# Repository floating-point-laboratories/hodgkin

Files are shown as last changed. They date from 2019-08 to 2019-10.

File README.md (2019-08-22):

# Project Hodgkin
Project Hodgkin is an open-source (semi) Arduino Nano compatible microcontroller development board that is developed to IEC 60601 standards for 2xMOPP (methods of patient protection) isolation. It is intended for educational settings to enable students and enthusiasts to safely interface with biopotential amplifier circuits.

**Will this device be IEC 60601 certified / FDA cleared / etc.?**
*Due to the nature of this device's application, which is to enable students to interface with biomedical electronics which they have designed and built themselves, it is not practical to pursue any form of formal medical device certification. This device's performance will depend entirely on the quality of the circuits that it is attached to; it therefore cannot and should not be used as a substitute for any medical device for diagnostic or therapeutic purposes. The intention of this project is to provide a safe interface between these experimental circuits and a computer via USB interface so that users are not exposed to dangerous voltages or currents in the case of PC power supply failure or mains power surge.*

**What do you mean "semi" Arduino Nano compatible?**
*This device is planned to share a pinout, footprint, and firmware with the Arduino Nano V3.0 (based on the ATmega328p microcontroller). However, some changes will be necessary to ensure safe operation of the device while maintaining low cost. These include the inability to draw microcontroller power from the on-board USB port, and incompatibility with shields / expansion boards which are connected to mains power.*

**Why use an optical link? Why not use a wireless connection like BLE?**
*This is something that was certainly considered, but was ultimately abandoned in favor of a direct optical serial link for three primary reasons:*

*1. Cost. The goal for this project is to meet the necessary safety requirements without dramatically adding to the cost of an Arduino Nano. Obviously some added costs are unavoidable, but a full RF solution was deemed an uneccessary cost.*

*2. Stability. Since this project is intended as a direct Aduino Nano substitute for use by students, it was important to us that it behave as similarly to a stock Arduino as possible. This means plug-and-play direct USB-to-serial simplicity whenever possible.*

*3. Security. Athough this device is not intended for use as a medical device, it is built with similar design philosophies in mind. In general, wireless solutions are typically not implemented in medical devices unless there is a compelling reason to do so to avoid potential data leaks / HIPAA violations.*

**When can I purchase this device?**
*This device is planned for inclusion in the electronics kit given to all students enrolled in SBEE 2020. Standalone sale of the device will certainly be considered if there is a demand for it. In the meantime, you are welcome to build one yourself using the files available in this repository.*

## About The Shoulders of Giants
In 1676, Isaac Newton, one of the most influential mathematicians and scientists of all time, famously wrote:

> "If I have seen further, it is by standing on the shoulders of giants."

The Shoulders of Giants, Inc. (TSoG) is a nonprofit (501(c)(3)) organization founded in 2013 on a vision that world-class science education should be available to all students of all ages. Since 2015, The Shoulders of Giants has offered an immersive, ongoing mentorship program for dedicated students who would like the opportunity to study more closely under the guidance of Dr. Steven J. Foland. This program is designed to provide middle and high school students with a broad foundation of knowledge and skills across science and engineering disciplines, experience working and communicating in a professional environment, and helps them develop the study habits necessary to achieve success at the university level and beyond.

In 2019, this world-class program became available to students everywhere with the launch of TSoG.tv. This online platform, created in collaboration between The Shoulders of Giants, Inc. and its sister-company Floating Point Laboratories, LLC, provides at-home exercises, live-streaming, and project support to students anywhere in the world.

## About #SBEE2020
Since 2015, The Shoulders of Giants has offered its flagship summer program, the Summer Biomedical Engineering Experience (SBEE) to high school students interested in exploring careers in biomedical engineering and related medical sciences. The original contents of the program were 60 hours of rigorous curriculum covering biomedical electronics, mechanical CAD and 3D printing, and microcontroller programming. Through this program, nearly 400 students have designed and built their own electromyograph (EMG) controlled prosthetic hands. 

In spring 2019, TSoG co-founder and Floating Point Laboratories managing director Dr. Steven J. Foland [announced an initiative](https://www.youtube.com/watch?v=rmPsDaRs3cc) to develop the SBEE curriculum into a TSoG.tv experience for students around the world in summer 2020. This has become known as the #SBEE2020 initiative. Dr. Foland hosted a successful 24-hour livestream fundraiser on June 29-30th 2019, teaching a prototype SBEE 2020 curriculum in one marathon session which can be viewed [here](https://www.tsogiants.org/2019/07/02/24-hour-challenge-physiological-signals-and-biomedical-electronics/). 

As of August 2019, development for SBEE 2020 is currently underway. In order to best serve the community, several new devices need to be developed to provide safe, affordable access to the technologies necessary for students to explore and interface with human biosignals. Among these are: Project Hodgkin, an inexpensive Arduino compatible microcontroller development board built to follow IEC 60601 safety standards; and Project Huxley, a USB oscilloscope developed with biomedical applications and safety standards in mind.

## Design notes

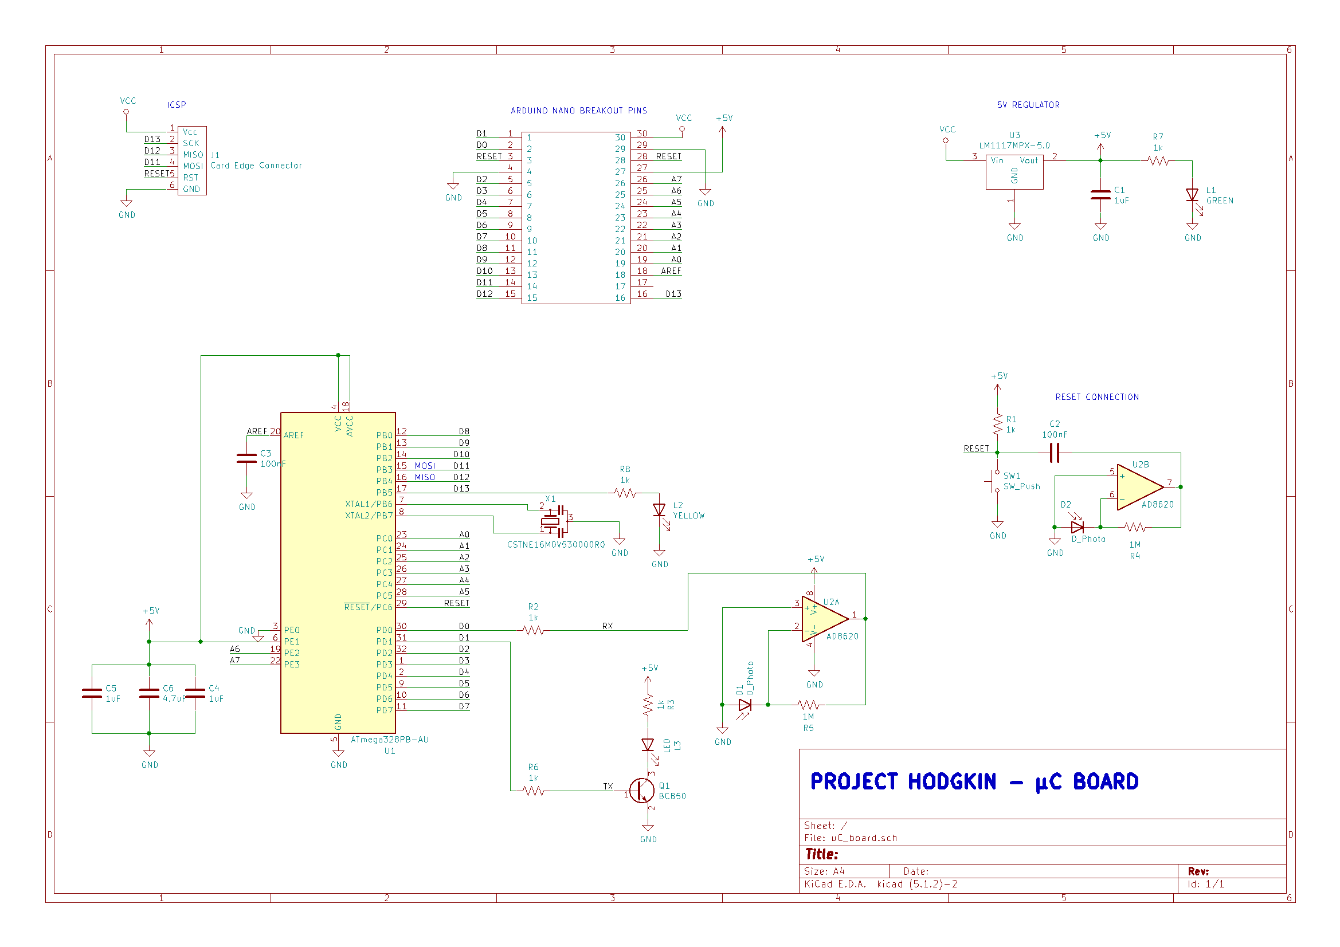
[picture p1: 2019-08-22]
_Media/uC_Board_Schematic.png

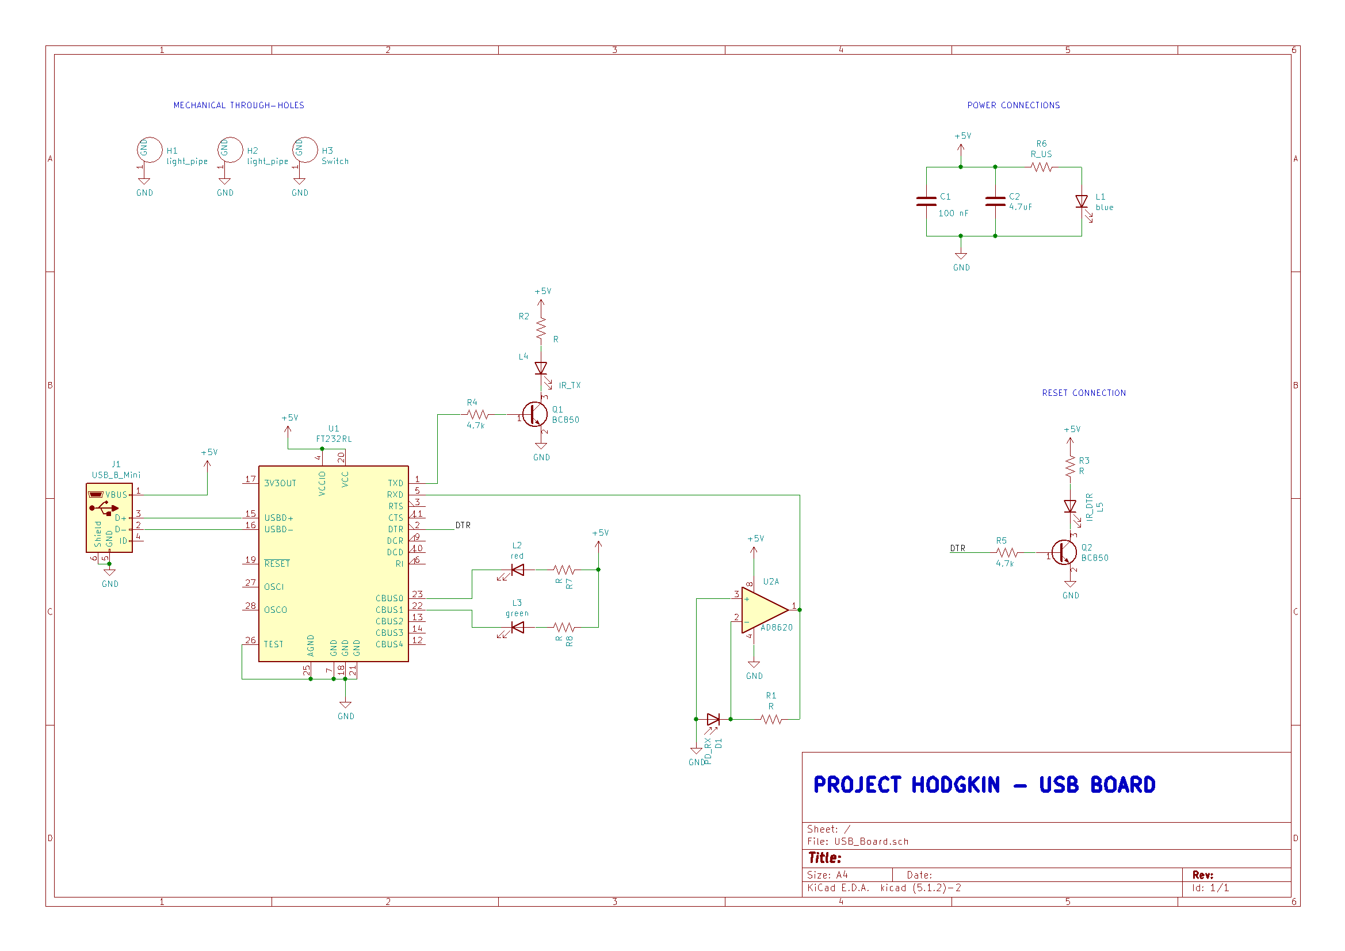
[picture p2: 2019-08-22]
_Media/USB_Board_Schematic.png

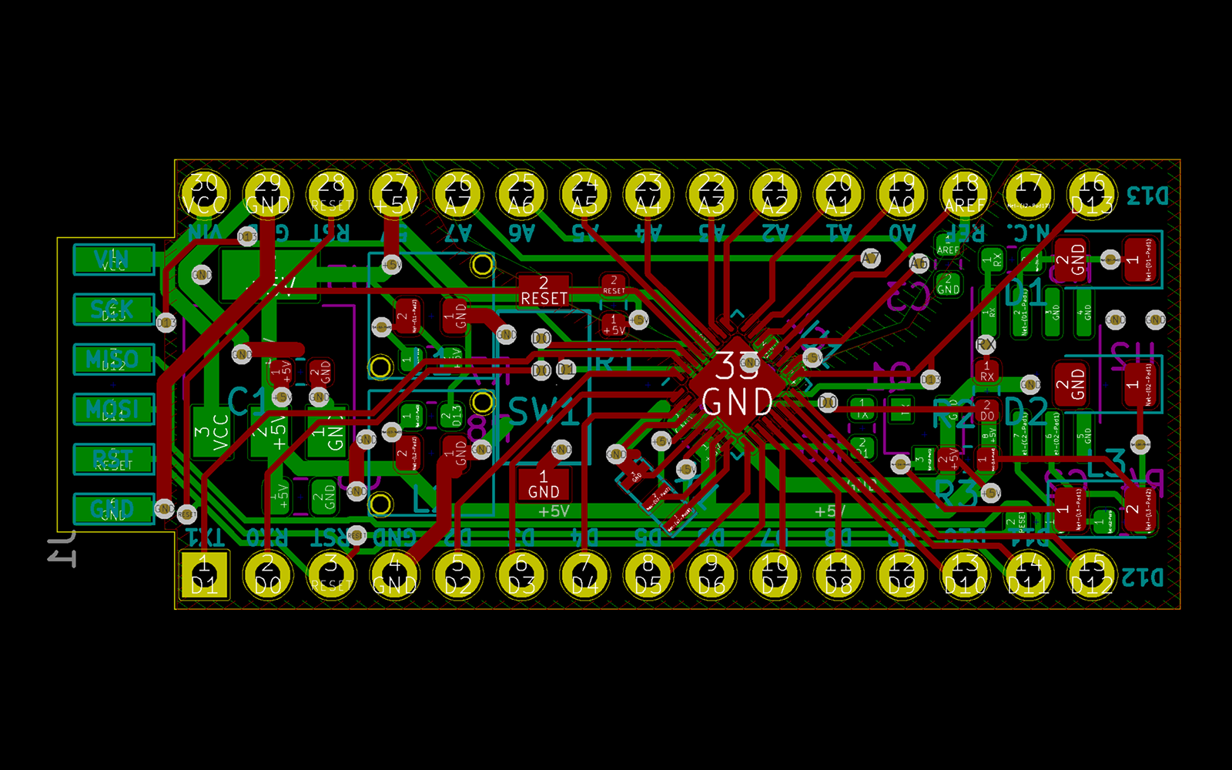
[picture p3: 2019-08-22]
_Media/uC_Board_Layout.png

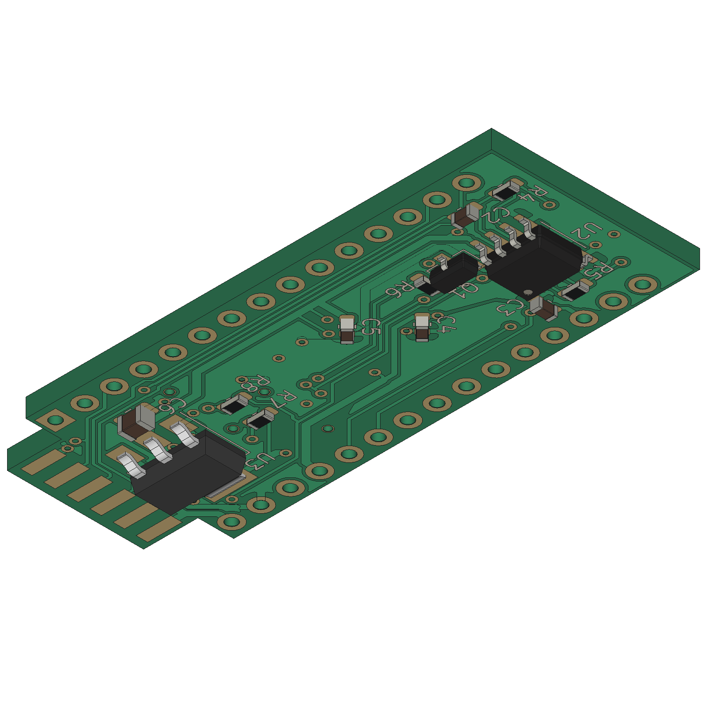
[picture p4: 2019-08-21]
_Media/uC_Board_bottom.png

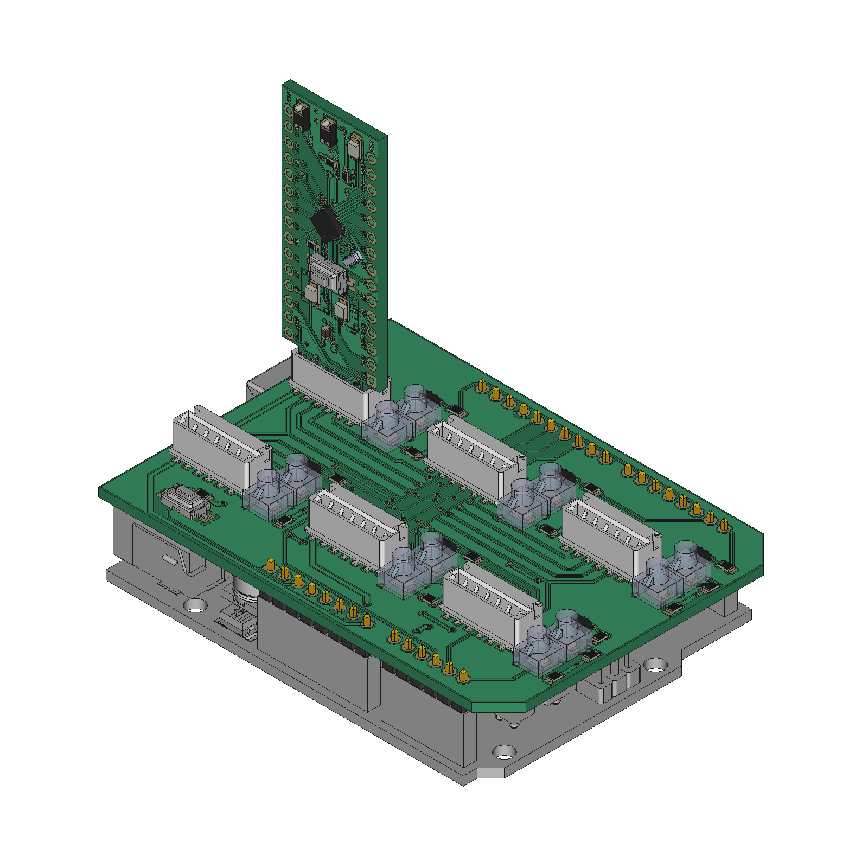
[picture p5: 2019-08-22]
_Media/ICSP_Board_withuC.png

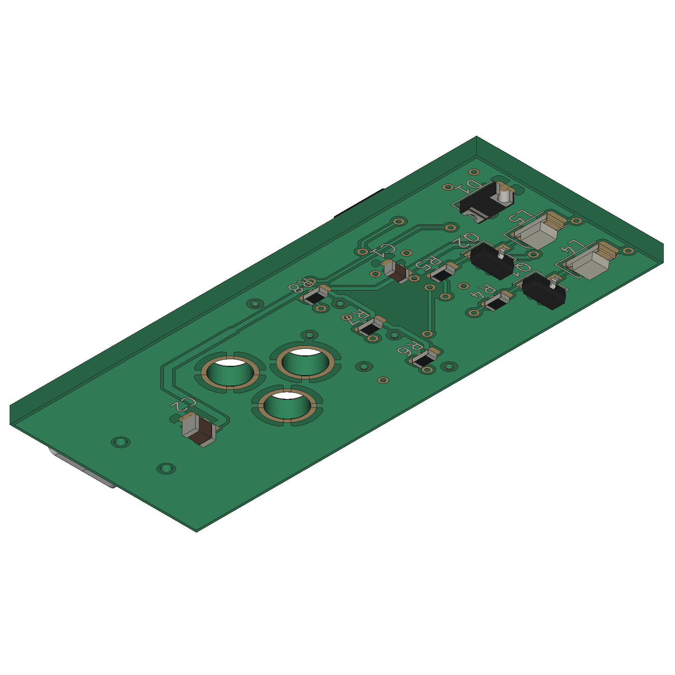
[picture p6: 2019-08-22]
_Media/USB_Board_Bottom.png

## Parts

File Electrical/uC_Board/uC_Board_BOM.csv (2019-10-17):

Description | Manufacturer | Man. Part # | Distributor | Dist. Part # | Link | Unit Price (@ 1) | Unit Price (@ 1000) | Quantity | Cost (@ 1) | Cost (@ 1000)
ATMEGA328 uC | Micochip Technology / Atmel | ATMEGA328PB-AU | Mouser | 556-ATMEGA328PB-AU | https://www.mouser.com/ProductDetail/Microchip-Technology-Atmel/ATMEGA328PB-AU?qs=jy4bLUHv09hbFONgGrqPbw%3D%3D | $1.38 | $1.150 | 1 | $1.38 | $1.150
Precision Transimpedance Amp | Texas Instruments | OPA2381AIDGKR | Mouser | 595-OPA2381AIDGKR | https://www.mouser.com/ProductDetail/Texas-Instruments/OPA2381AIDGKR | $2.68 | $1.410 | 1 | $2.68 | $1.410
IR Photodiode | Wurth Elektronik | 1541201EEA400 | Mouser | 710-1541201EEA400 | https://www.mouser.com/ProductDetail/Wurth-Elektronik/1541201EEA400 | $0.54 | $0.330 | 2 | $1.08 | $0.660
IR LED | Stanley Electric | TAN1105W-TR | Mouser | 327-TAN1105WTR | https://www.mouser.com/ProductDetail/Stanley-Electric/TAN1105W-TR | $0.37 | $0.123 | 1 | $0.37 | $0.123
NPN BJT | ON Semiconductor | BC850CLT1G | Mouser | 863-BC850CLT1G | https://www.mouser.com/ProductDetail/ON-Semiconductor/BC850CLT1G | $0.10 | $0.020 | 1 | $0.10 | $0.020
3.3V LDO Regulator | Texas Instruments | LM1117MPX-5.0/NOPB | Mouser | 926-LM1117MPX5.0NOPB | https://www.mouser.com/ProductDetail/Texas-Instruments/LM1117MPX-50-NOPB?qs=X1J7HmVL2ZE1O12Qsl7F9g%3D%3D | $1.10 | $0.501 | 1 | $1.10 | $0.501
16MHz oscillator | Murata Electronics | CSTNE16M0V530000R0 | Mouser | 81-CSTNE16M0V530000R | https://www.mouser.com/ProductDetail/Murata-Electronics/CSTNE16M0V530000R0 | $0.51 | $0.269 | 1 | $0.51 | $0.269
pushbutton switch | C&K | PTS636 SK25 SMTR LFS | Mouser | 611-PTS636SK25SMTRLF | https://www.mouser.com/ProductDetail/CK/PTS636-SK25-SMTR-LFS | $0.13 | $0.076 | 1 | $0.13 | $0.076
light pipe | Bivar | VLP-650-F | Digi-Key | 492-2287-ND | https://www.digikey.com/product-detail/en/bivar-inc/VLP-650-F/492-2287-ND/4500883 | $0.53 | $0.170 | 2 | $1.06 | $0.340
1uF capacitor 0603 |  |  |  |  |  |  |  | 3
4.7uF capacitor 0805 |  |  |  |  |  |  |  | 1
100nF capacitor 0603 |  |  |  |  |  |  |  | 1
1k resistor 0603 |  |  |  |  |  |  |  | 5
1M resistor 0603 |  |  |  |  |  |  |  | 2
Single row male header pins |  |  |  |  |  |  |  | 2
 |  |  |  |  |  |  |  |  | $8.81 | $4.769

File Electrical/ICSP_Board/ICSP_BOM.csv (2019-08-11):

Description | Manufacturer | Man. Part # | Distributor | Dist. Part # | Link | Unit Price (@ 1) | Quantity | Cost
Card Edge Connector | AVX | 6.09E+14 | Mouser | 581-609159350609000 | https://www.mouser.com/ProductDetail/AVX/609159350609000 | $0.18 | 1 | $0.18
Header Pins | TE Connectivity | 4-103741-0 | Mouser | 571-41037410 | https://www.mouser.com/ProductDetail/TE-Connectivity/4-103741-0 | $2.04 | 1 | $2.04
PCB | TBD | N/A | N/A | N/A | Custom | TBD | 1 | TBD

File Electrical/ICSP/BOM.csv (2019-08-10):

Description | Manufacturer | Man. Part # | Distributor | Dist. Part # | Link | Unit Price (@ 1) | Quantity | Cost
Card Edge Connector | AVX | 6.09E+14 | Mouser | 581-609159350609000 | https://www.mouser.com/ProductDetail/AVX/609159350609000 | $0.18 | 1 | $0.18
Header Pins | TE Connectivity | 4-103741-0 | Mouser | 571-41037410 | https://www.mouser.com/ProductDetail/TE-Connectivity/4-103741-0 | $2.04 | 1 | $2.04
PCB | TBD | N/A | N/A | N/A | Custom | TBD | 1 | TBD
FT232RL | FTDI | N/A | Mouser | 895-FT232RL | https://www.mouser.com/ProductDetail/FTDI/FT232RL-REEL | $4.50 | 1 | $4.50
MF-MSMF050-2 | Bourns | MF-MSMF050-2 | Mouser | 652-MF-MSMF050-2 | https://www.mouser.com/ProductDetail/Bourns/MF-MSMF050-2?qs=t3shhpq1i1DZ7OBD5kLNoA%3D%3D | $0.45 | 1 | $0.45

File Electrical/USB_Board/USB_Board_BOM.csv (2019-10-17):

Description | Manufacturer | Man. Part # | Distributor | Dist. Part # | Link | Unit Price (@ 1) | Unit Price (@ 1000) | Quantity | Cost (@ 1) | Cost (@ 1000)
USB RS232 Interface IC | FTDI | FT232RL | Mouser | 895-FT232RL | https://www.mouser.com/ProductDetail/FTDI/FT232RL-REEL | $4.50 | $2.65 | 1 | $4.50 | $2.650
Precision Transimpedance Amp | Texas Instruments | OPA2381AIDGKR | Mouser | 595-OPA2381AIDGKR | https://www.mouser.com/ProductDetail/Texas-Instruments/OPA2381AIDGKR | $2.68 | $1.410 | 1 | $2.68 | $1.410
IR Photodiode | Wurth Elektronik | 1541201EEA400 | Mouser | 710-1541201EEA400 | https://www.mouser.com/ProductDetail/Wurth-Elektronik/1541201EEA400 | $0.54 | $0.33 | 1 | $0.54 | $0.330
IR LED | Stanley Electric | TAN1105W-TR | Mouser | 327-TAN1105WTR | https://www.mouser.com/ProductDetail/Stanley-Electric/TAN1105W-TR | $0.37 | $0.12 | 2 | $0.74 | $0.246
NPN BJT | ON Semiconductor | BC850CLT1G | Mouser | 863-BC850CLT1G | https://www.mouser.com/ProductDetail/ON-Semiconductor/BC850CLT1G | $0.10 | $0.02 | 2 | $0.20 | $0.050
 |  |  |  |  |  |  |  |  | $9.06 | $4.906

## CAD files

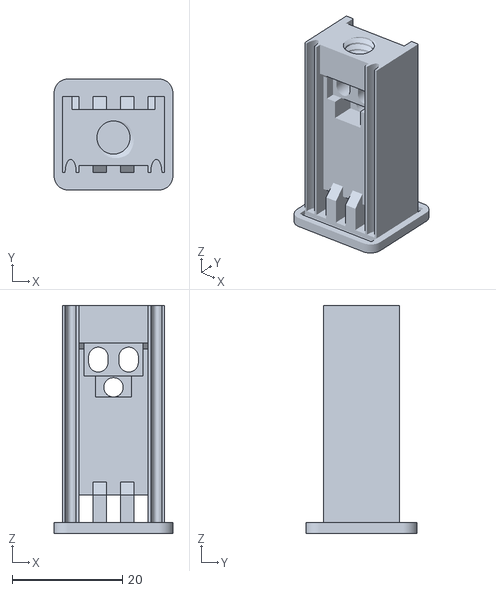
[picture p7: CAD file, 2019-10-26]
Mechanical/CAM/Hodgkin/STL/Housing_Main.stl
21.5 x 20.1 x 41.3

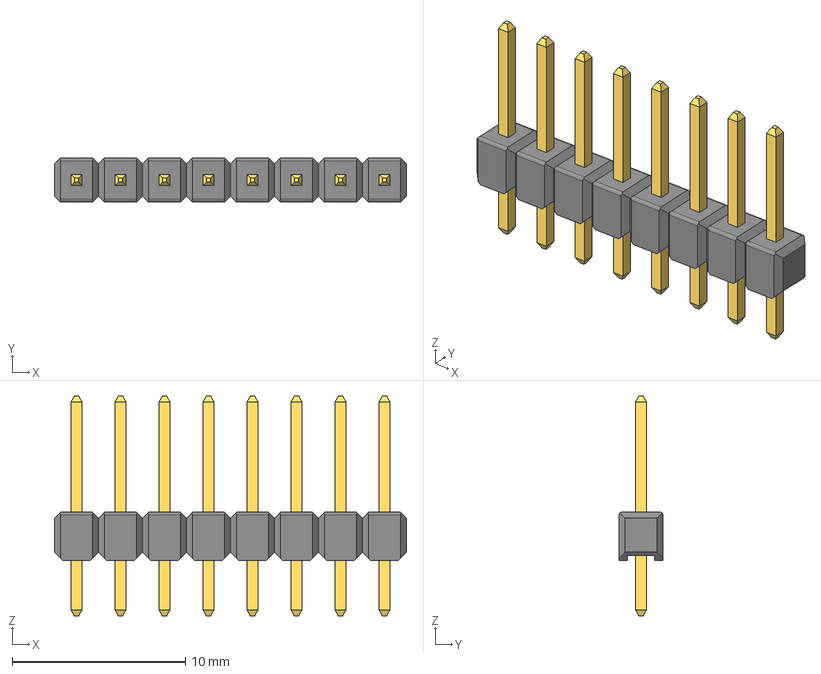
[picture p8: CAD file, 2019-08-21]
Electrical/_lib/3D/Pin Header 1x8 TH Pitch 2.54mm.stp
20.3 x 2.54 x 12.7 mm

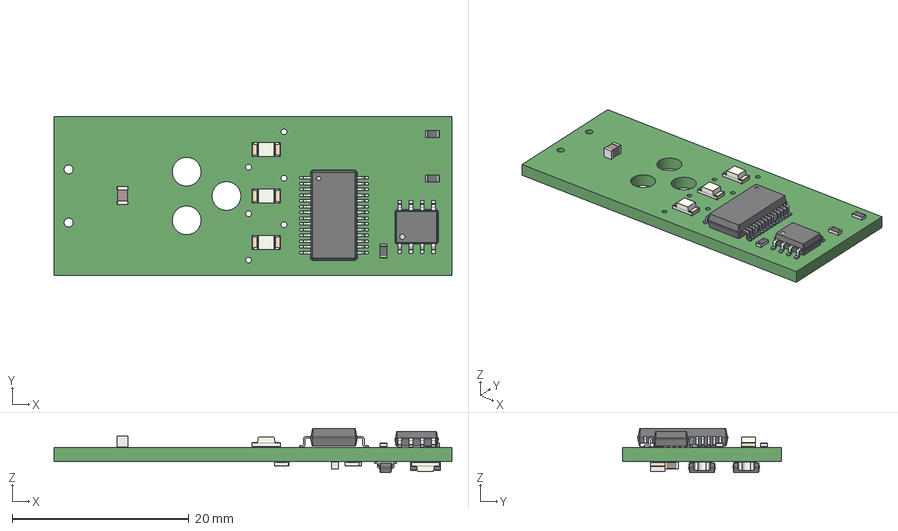
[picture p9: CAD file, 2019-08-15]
Electrical/USB_Board/USB_Board_1.step
45.0 x 18.0 x 5.00 mm

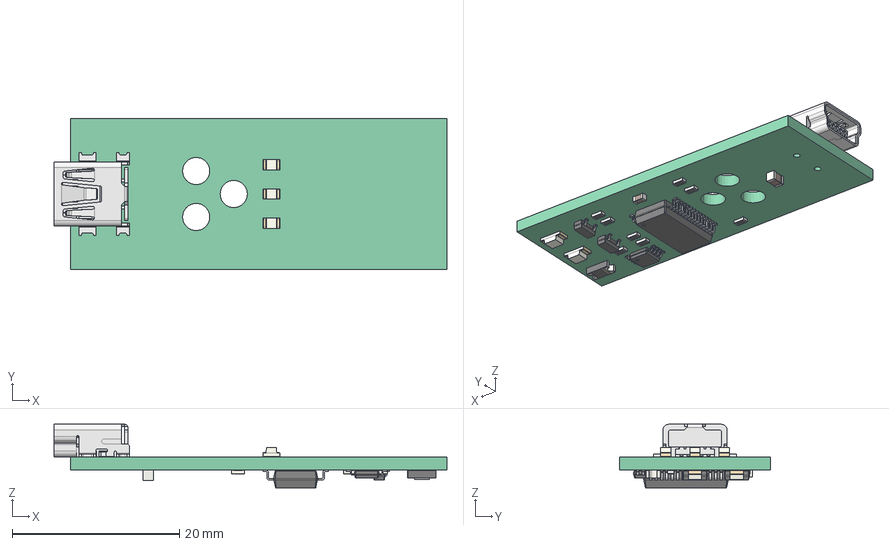
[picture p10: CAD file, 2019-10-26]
Mechanical/Hodgkin/Hodgkin_Housing/PCB_Assembly_Alibre/USB_Board.stp
47.0 x 18.0 x 7.60 mm
Open_CASCADE_STEP_translator_7.3_3.1.2.1
J1_Molex67503-1020_5D522559
L3_LED_0805_2012Metric_5DA8ECDF
L2_LED_0805_2012Metric_5D522524
L1_LED_0805_2012Metric_5D523A45
U2_MSOP_8_3x3mm_P065mm_5DA8BF9B
L5_LED_1206_3216Metric_5D52257F
L4_LED_1206_3216Metric_5D562A63
D1_D_1206_5D522511
U1_SSOP_28_53x102mm_P065mm_5DA8CDAA
C2_C_0805_2012Metric_5D560A4C
R5_R_0603_1608Metric_5D522631
R4_R_0603_1608Metric_5D522620
R8_R_0603_1608Metric_5DA8CCE2
R7_R_0603_1608Metric_5D5225FE
R3_R_0603_1608Metric_5D5225ED
R1_R_0603_1608Metric_5D5225DC
R2_R_0603_1608Metric_5D5225CB
R6_R_0603_1608Metric_5D5225BA
Q2_SOT_23_5DA97F1F
Q1_SOT_23_5D522594
C1_C_0603_1608Metric_5DA8E52C

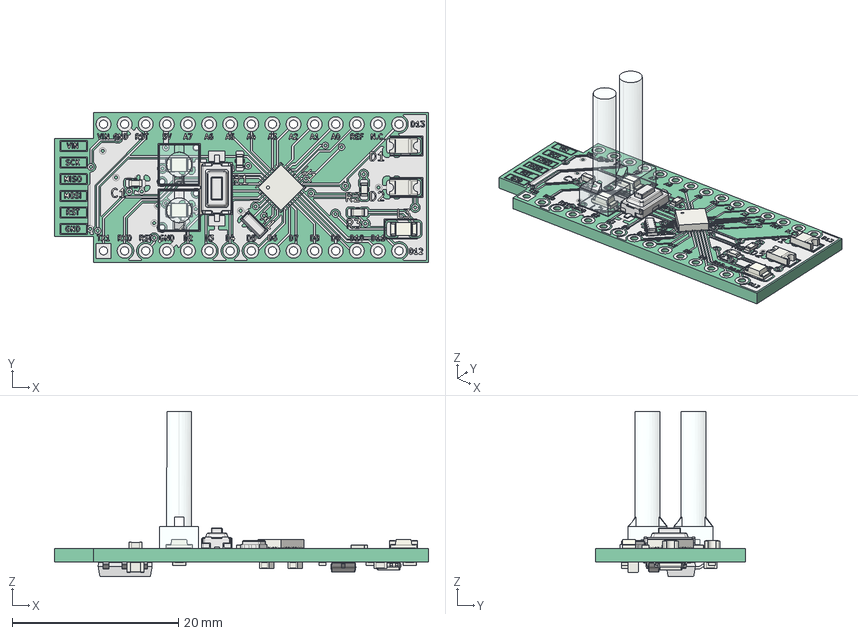
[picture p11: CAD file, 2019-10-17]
Mechanical/Hodgkin/uC_Board/uC_Board.FCStd
45.0 x 18.0 x 19.9 mm
Pcb
topTracks
botTracks
botSilks
topSilks
L3_LED_1206_3216Metric_5D5B449F
L1_LED_1206_3216Metric_5D520C8B
L1_VLP-650-F_5D520C8B[2]
L2_LED_1206_3216Metric_5D5207AE
L2_VLP-650-F_5D5207AE[2]
PTS636SK25FSMTRLFS
R1_R_0603_1608Metric_5D55EB9F
C1_C_0603_1608Metric_5D520950
R3_R_0603_1608Metric_5D5AFE69
R2_R_0603_1608Metric_5D562464
U1_QFN_32_1EP_4x4mm_P04mm_EP29x29mm_5D520A1B
CSTNE16M0V530000R0--3DModel-STEP-56544
D2_D_1206_5D5209B7
D1_D_1206_5D520ACE
U2_MSOP_8_3x3mm_P065mm_5DA8BF72
LM1117MP-3.3--3DModel-STEP-56544
R4_R_0603_1608Metric_5D5B44F5
R7_R_0603_1608Metric_5D56099D
R5_R_0603_1608Metric_5D52089C
Q1_SOT_23_5D5B56B7
C2_C_0603_1608Metric_5D521224
C3_C_0603_1608Metric_5D584ECB
C4_C_0603_1608Metric_5D51E594
C6_C_0805_2012Metric_5D55E95F
C5_C_0603_1608Metric_5D50C931
R6_R_0603_1608Metric_5D560222
R8_R_0603_1608Metric_5D50CA13

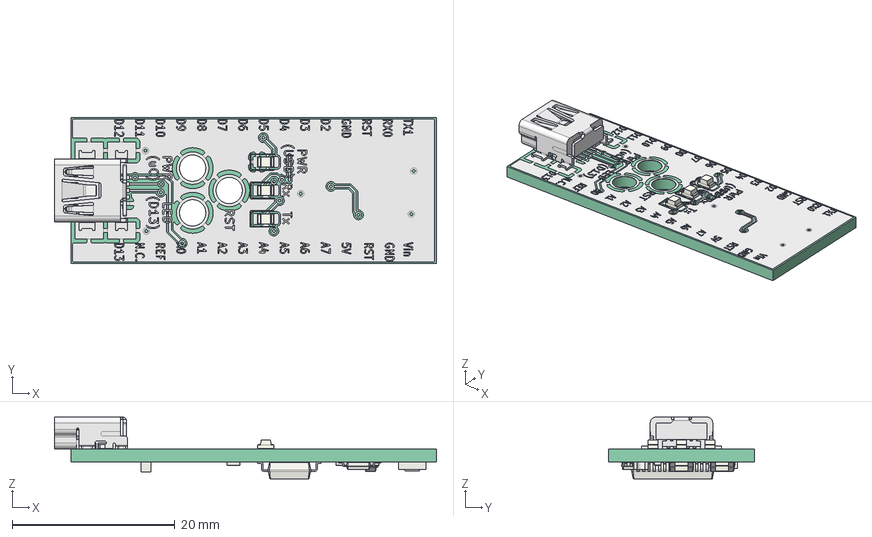
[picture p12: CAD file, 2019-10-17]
Mechanical/Hodgkin/USB_Board/USB_Board.FCStd
47.0 x 18.0 x 7.60 mm
Pcb
topTracks
botTracks
botSilks
topSilk
J1_Molex67503-1020_5D522559
L3_LED_0805_2012Metric_5DA8ECDF
L2_LED_0805_2012Metric_5D522524
L1_LED_0805_2012Metric_5D523A45
U2_MSOP_8_3x3mm_P065mm_5DA8BF9B
L5_LED_1206_3216Metric_5D52257F
L4_LED_1206_3216Metric_5D562A63
D1_D_1206_5D522511
U1_SSOP_28_53x102mm_P065mm_5DA8CDAA
C2_C_0805_2012Metric_5D560A4C
R5_R_0603_1608Metric_5D522631
R4_R_0603_1608Metric_5D522620
R8_R_0603_1608Metric_5DA8CCE2
R7_R_0603_1608Metric_5D5225FE
R3_R_0603_1608Metric_5D5225ED
R1_R_0603_1608Metric_5D5225DC
R2_R_0603_1608Metric_5D5225CB
R6_R_0603_1608Metric_5D5225BA
Q2_SOT_23_5DA97F1F
Q1_SOT_23_5D522594
C1_C_0603_1608Metric_5DA8E52C

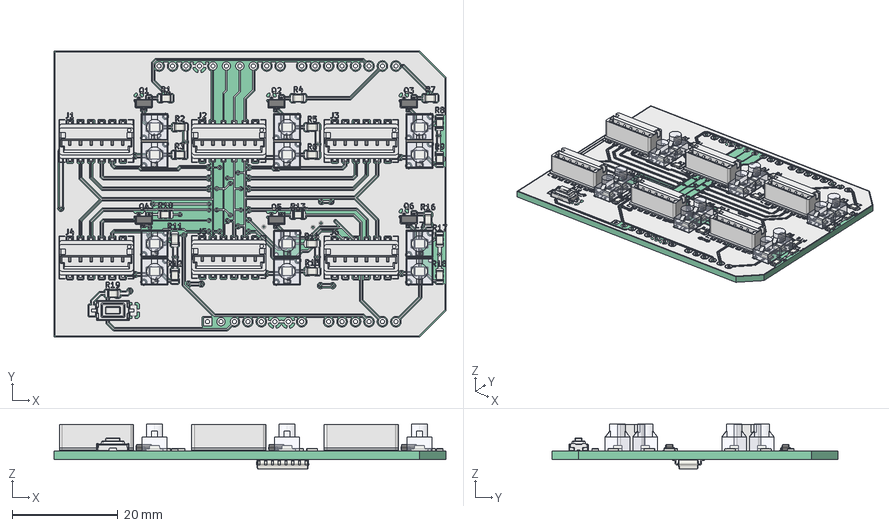
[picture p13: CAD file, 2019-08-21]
Mechanical/ICSP/ICSP_Board/ICSP_Board.FCStd
74.2 x 54.0 x 8.43 mm
Pcb
topTracks
botTracks
botSilks
topSilks
R2_R_0805_2012Metric_5D50C32D
SW1_PTS636SK25FSMTRLFS_5D5C95BF
R19_R_0805_2012Metric_5D5C95B5
R13_R_0805_2012Metric_5D5C95A4
R7_R_0805_2012Metric_5D5C9593
R1_R_0805_2012Metric_5D5C9582
R10_R_0805_2012Metric_5D5C9571
R4_R_0805_2012Metric_5D5C9560
R16_R_0805_2012Metric_5D5C954F
Q5_SOT_23_5D5CDDBF
Q3_SOT_23_5D5C9409
Q1_SOT_23_5D5C93F4
Q6_SOT_23_5D5C93DF
Q4_SOT_23_5D5C93CA
Q2_SOT_23_5D5C93B5
L12_LED_1206_3216Metric_5D50C157
L12_VLP-200-F_5D50C157[2]
L11_LED_1206_3216Metric_5D50DA63
L11_VLP-200-F_5D50DA63[2]
L10_LED_1206_3216Metric_5D50C17D
L10_VLP-200-F_5D50C17D[2]
L9_LED_1206_3216Metric_5D50DAD1
L9_VLP-200-F_5D50DAD1[2]
L8_LED_1206_3216Metric_5D50C1A3
L8_VLP-200-F_5D50C1A3[2]
L7_LED_1206_3216Metric_5D50C1B6
L7_VLP-200-F_5D50C1B6[2]
L2_LED_1206_3216Metric_5D50C63E
L2_VLP-200-F_5D50C63E[2]
L1_LED_1206_3216Metric_5D50C6AA
L1_VLP-200-F_5D50C6AA[2]
L6_LED_1206_3216Metric_5D50C144
L6_VLP-200-F_5D50C144[2]
L5_LED_1206_3216Metric_5D50DB40
L5_VLP-200-F_5D50DB40[2]
L4_LED_1206_3216Metric_5D50C8CF
L4_VLP-200-F_5D50C8CF[2]
L3_LED_1206_3216Metric_5D50D0E6
L3_VLP-200-F_5D50D0E6[2]
R17_R_0805_2012Metric_5D5DC9E7
R14_R_0805_2012Metric_5D50C371
R11_R_0805_2012Metric_5D50C360
R8_R_0805_2012Metric_5D50C34F
R5_R_0805_2012Metric_5D50DC6C
R18_R_0805_2012Metric_5D5DCA1A
R15_R_0805_2012Metric_5D50C30B
R12_R_0805_2012Metric_5D50C2FA
R9_R_0805_2012Metric_5D50C2E9
R6_R_0805_2012Metric_5D50DC0B
R3_R_0805_2012Metric_5D50C2C7
J6_AVX-00-9159-006-551-906_5D50B2F3
J5_AVX-00-9159-006-551-906_5D50B2E3
J4_AVX-00-9159-006-551-906_5D50B2D3
J3_AVX-00-9159-006-551-906_5D50D119
J2_AVX-00-9159-006-551-906_5D50C737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

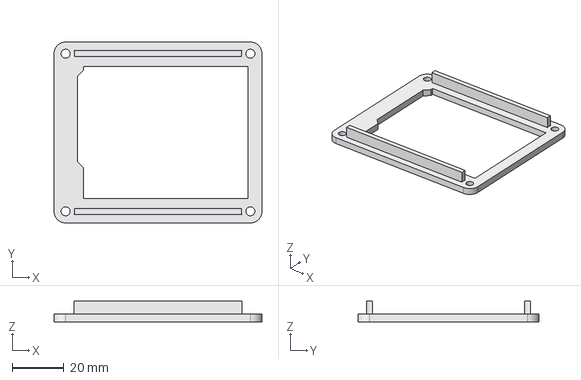
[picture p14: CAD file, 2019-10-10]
Mechanical/ICSP/ICSP_Housing/ICSP_Housing_Spacer.step
80.5 x 70.0 x 8.00 mm

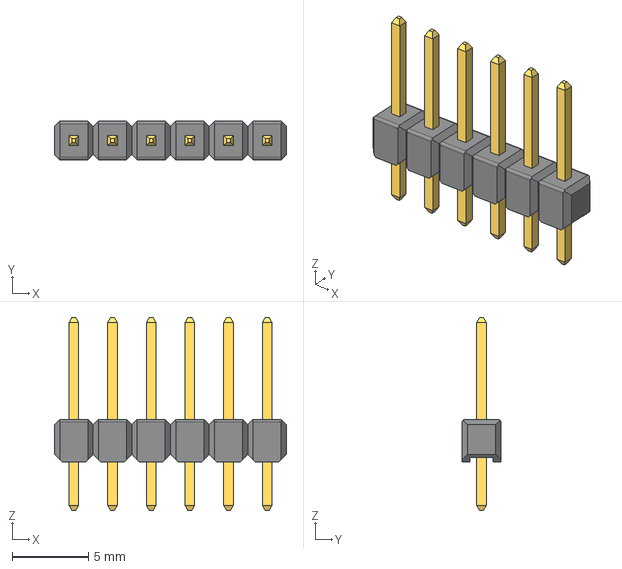
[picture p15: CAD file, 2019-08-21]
Electrical/_lib/3D/Pin Header 1x6 TH Pitch 2.54mm.stp
15.2 x 2.54 x 12.7 mm

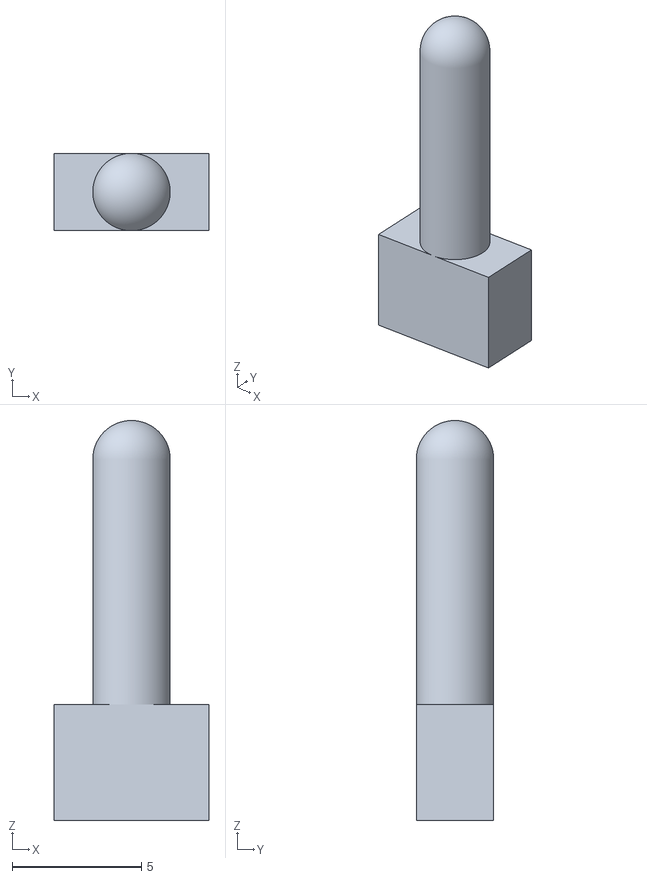
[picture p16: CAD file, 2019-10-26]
Mechanical/CAM/Hodgkin/STL/Button.stl
6.00 x 3.00 x 15.5

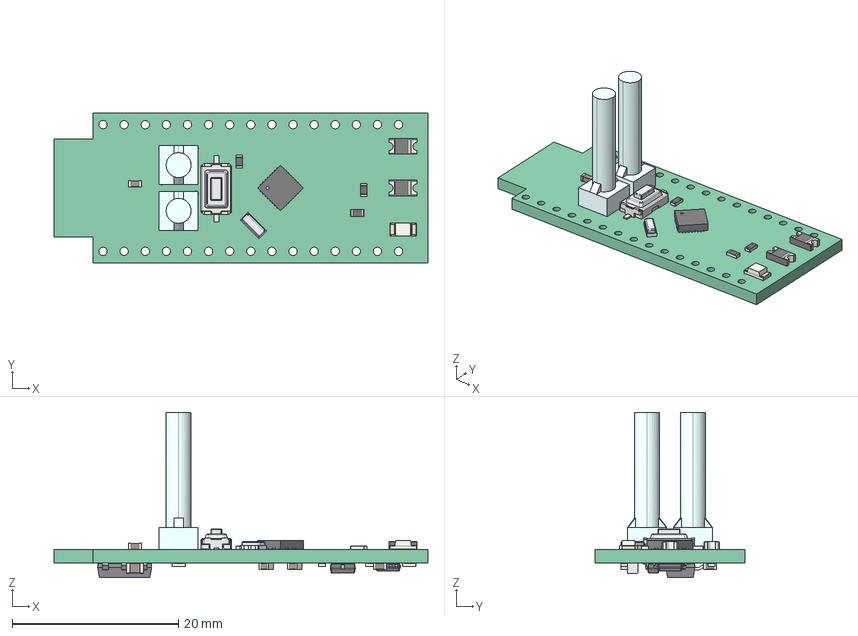
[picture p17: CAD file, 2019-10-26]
Mechanical/Hodgkin/Hodgkin_Housing/PCB_Assembly_Alibre/uC_board.stp
45.0 x 18.0 x 19.9 mm
PCB_Sketch
L3_LED_1206_3216Metric_5D5B449F
L1_LED_1206_3216Metric_5D520C8B
L1_VLP-650-F_5D520C8B[2]
L2_LED_1206_3216Metric_5D5207AE
L2_VLP-650-F_5D5207AE[2]
PTS636SK25FSMTRLFS
PTS636SK25FSMTRLFS_2
PTS636SK25FSMTRLFS_3
PTS636SK25FSMTRLFS_4
PTS636SK25FSMTRLFS_5
PTS636SK25FSMTRLFS_6
PTS636SK25FSMTRLFS_7
PTS636SK25FSMTRLFS_8
PTS636SK25FSMTRLFS_9
PTS636SK25FSMTRLFS_10
PTS636SK25FSMTRLFS_11
PTS636SK25FSMTRLFS_12
PTS636SK25FSMTRLFS_13
R1_R_0603_1608Metric_5D55EB9F
C1_C_0603_1608Metric_5D520950
R3_R_0603_1608Metric_5D5AFE69
R2_R_0603_1608Metric_5D562464
U1_QFN_32_1EP_4x4mm_P04mm_EP29x29mm_5D520A1B
CSTNE16M0V530000R0--3DModel-STEP-56544
CSTNE16M0V530000R0--3DModel-STEP-56544_2
CSTNE16M0V530000R0--3DModel-STEP-56544_3
CSTNE16M0V530000R0--3DModel-STEP-56544_4
CSTNE16M0V530000R0--3DModel-STEP-56544_5
CSTNE16M0V530000R0--3DModel-STEP-56544_6
CSTNE16M0V530000R0--3DModel-STEP-56544_7
CSTNE16M0V530000R0--3DModel-STEP-56544_8
CSTNE16M0V530000R0--3DModel-STEP-56544_9
CSTNE16M0V530000R0--3DModel-STEP-56544_10
CSTNE16M0V530000R0--3DModel-STEP-56544_11
CSTNE16M0V530000R0--3DModel-STEP-56544_12
CSTNE16M0V530000R0--3DModel-STEP-56544_13
CSTNE16M0V530000R0--3DModel-STEP-56544_14
CSTNE16M0V530000R0--3DModel-STEP-56544_15
D2_D_1206_5D5209B7
D1_D_1206_5D520ACE
U2_MSOP_8_3x3mm_P065mm_5DA8BF72
LM1117MP-3.3--3DModel-STEP-56544
LM1117MP-3.3--3DModel-STEP-56544_2
LM1117MP-3.3--3DModel-STEP-56544_3
LM1117MP-3.3--3DModel-STEP-56544_4
LM1117MP-3.3--3DModel-STEP-56544_5
LM1117MP-3.3--3DModel-STEP-56544_6
LM1117MP-3.3--3DModel-STEP-56544_7
LM1117MP-3.3--3DModel-STEP-56544_8
LM1117MP-3.3--3DModel-STEP-56544_9
R4_R_0603_1608Metric_5D5B44F5
R7_R_0603_1608Metric_5D56099D
R5_R_0603_1608Metric_5D52089C
Q1_SOT_23_5D5B56B7
C2_C_0603_1608Metric_5D521224
C3_C_0603_1608Metric_5D584ECB
C4_C_0603_1608Metric_5D51E594
C6_C_0805_2012Metric_5D55E95F
C5_C_0603_1608Metric_5D50C931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

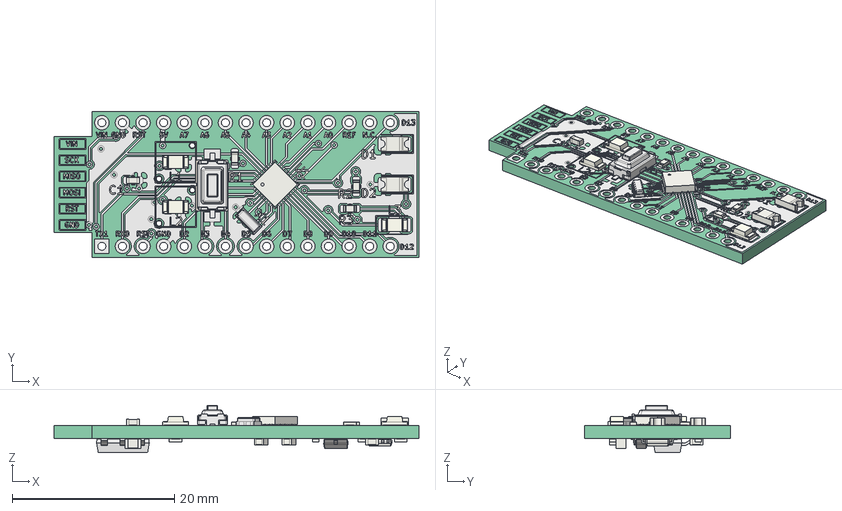
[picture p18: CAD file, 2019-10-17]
Mechanical/Hodgkin/uC_Board/uC_Board_no_LightPipes.FCStd
45.0 x 18.0 x 5.85 mm
Pcb
topTracks
botTracks
botSilks
topSilks
L3_LED_1206_3216Metric_5D5B449F
L1_LED_1206_3216Metric_5D520C8B
L2_LED_1206_3216Metric_5D5207AE
PTS636SK25FSMTRLFS
R1_R_0603_1608Metric_5D55EB9F
C1_C_0603_1608Metric_5D520950
R3_R_0603_1608Metric_5D5AFE69
R2_R_0603_1608Metric_5D562464
U1_QFN_32_1EP_4x4mm_P04mm_EP29x29mm_5D520A1B
CSTNE16M0V530000R0--3DModel-STEP-56544
D2_D_1206_5D5209B7
D1_D_1206_5D520ACE
U2_MSOP_8_3x3mm_P065mm_5DA8BF72
LM1117MP-3.3--3DModel-STEP-56544
R4_R_0603_1608Metric_5D5B44F5
R7_R_0603_1608Metric_5D56099D
R5_R_0603_1608Metric_5D52089C
Q1_SOT_23_5D5B56B7
C2_C_0603_1608Metric_5D521224
C3_C_0603_1608Metric_5D584ECB
C4_C_0603_1608Metric_5D51E594
C6_C_0805_2012Metric_5D55E95F
C5_C_0603_1608Metric_5D50C931
R6_R_0603_1608Metric_5D560222
R8_R_0603_1608Metric_5D50CA13

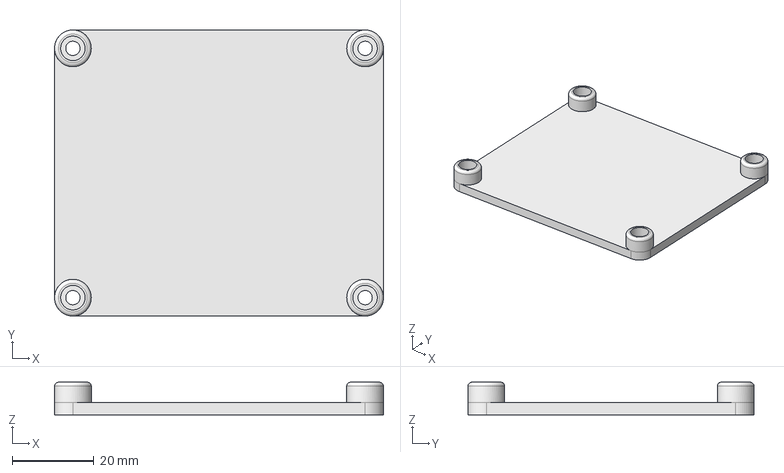
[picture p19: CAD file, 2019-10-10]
Mechanical/ICSP/ICSP_Housing/ICSP_Housing_Bottom.step
80.5 x 70.0 x 8.00 mm

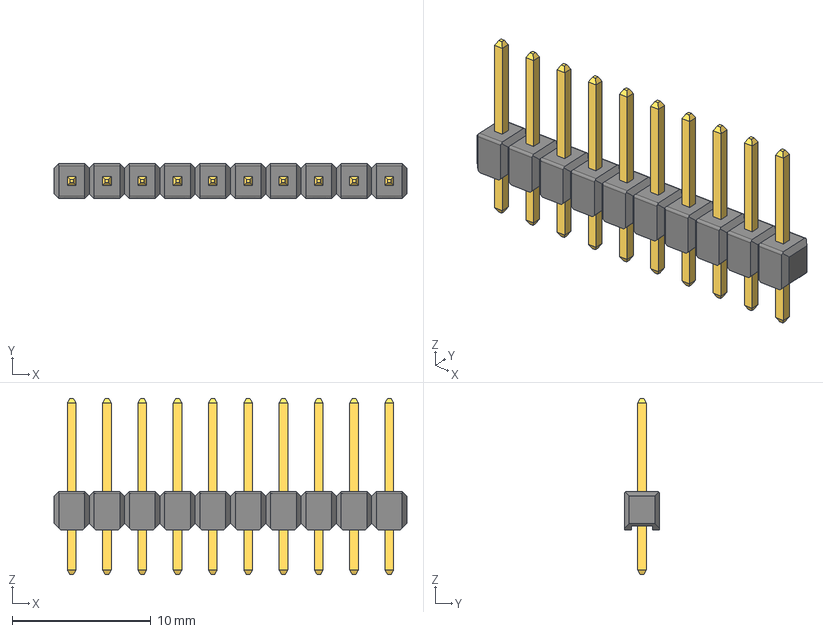
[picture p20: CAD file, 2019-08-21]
Electrical/_lib/3D/Pin Header 1x10 TH Pitch 2.54mm.stp
25.4 x 2.54 x 12.7 mm

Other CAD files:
Mechanical/CAM/Hodgkin/STL/Housing_Front.stl
Mechanical/ICSP/ICSP_Housing/ICSP_Housing_Top.step
Electrical/_lib/3D/AVX-00-9159-006-551-906.STEP
Mechanical/ICSP/ICSP_Housing/Housing_Button.FCStd
Electrical/_lib/3D/LM1117MP-3.3--3DModel-STEP-56544.STEP
Electrical/_lib/3D/Molex67503-1020.stp
Electrical/_lib/3D/PTS636SK25FSMTRLFS.stp
Electrical/_lib/3D/Pin Header 1x15 TH Pitch 2.54mm.stp
Electrical/_lib/3D/VLP-200-F.igs
Electrical/_lib/3D/VLP-650-F.igs
Mechanical/CAM/Hodgkin/STL/Screw.stl
Mechanical/Hodgkin/USB_Board/USB_Board-B_SilkS.dxf
Mechanical/Hodgkin/USB_Board/USB_Board-F_SilkS.dxf
Mechanical/Hodgkin/uC_Board/uC_board-B_SilkS.dxf
Mechanical/Hodgkin/uC_Board/uC_board-F_SilkS.dxf
Mechanical/ICSP/ICSP_Board/ICSP-B_SilkS.dxf
Mechanical/ICSP/ICSP_Board/ICSP-F_SilkS.dxf
Mechanical/ICSP/ICSP_Housing/Housing_Spacer.FCStd
Mechanical/ICSP/ICSP_Housing/ICSP_Housing_Bottom.FCStd
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

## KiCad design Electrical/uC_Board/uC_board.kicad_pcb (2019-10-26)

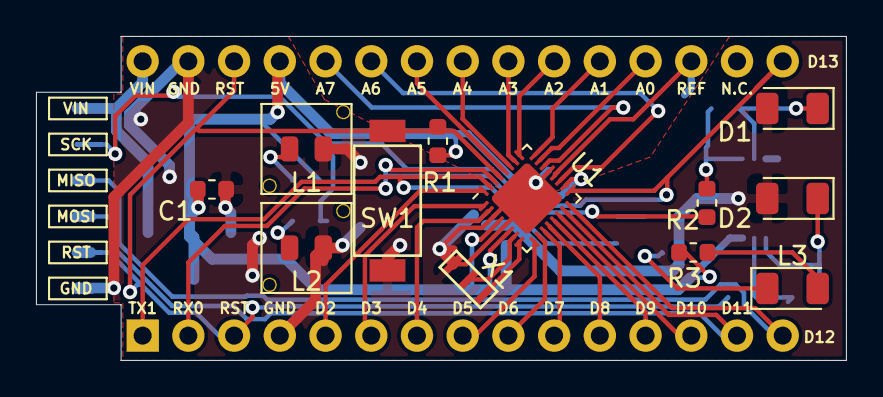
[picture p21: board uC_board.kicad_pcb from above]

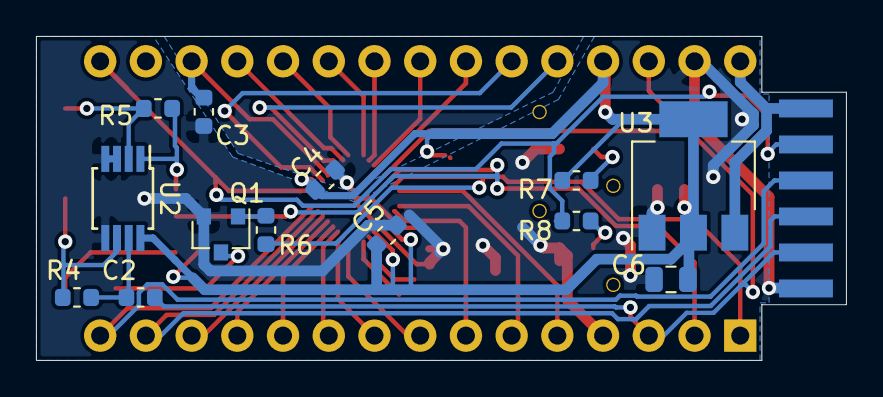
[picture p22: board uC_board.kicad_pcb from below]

Board: 2 copper layers, 45.0 x 18.0 mm, 27 parts (14 on the bottom side), 38 nets.

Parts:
C1, C4, C5: 1uF; C_0603_1608Metric
C2, C3: 100nF; C_0603_1608Metric
C6: 4.7uF; C_0805_2012Metric
D1, D2: D_Photo; D_1206_3216Metric
J1: Card Edge Connector; card_edge_6p_single_side
J2: Arduino Breakout Pins; ArdNanoStrip
L1: GREEN; LED_0805_LightPipe_Long
L2: YELLOW; LED_0805_LightPipe_Long
L3: LED; LED_1206_3216Metric
Q1: BC850; SOT-23
R1, R2, R3, R6, R7, R8: 1k; R_0603_1608Metric
R4, R5: 1M; R_0603_1608Metric
SW1: SW_Push; PTS636-G-2.5-NoGND
U1: ATmega328PB-AU; QFN-32-1EP_4x4mm_P0.4mm_EP2.9x2.9mm
U2: OPA2381; MSOP-8_3x3mm_P0.65mm
U3: LM1117MPX-5.0; LM1117
X1: CSTNE16M0V530000R0

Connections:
+5V: C1.1, C4.1, C5.1, C6.1, J2.27, R1.1, R3.2, R7.2, U1.4, U1.6, U1.18, U2.8, U3.2
/A0: J2.19, U1.23
/A1: J2.20, U1.24
/A2: J2.21, U1.25
/A3: J2.22, U1.26
/A4: J2.23, U1.27
/A5: J2.24, U1.28
/A6: J2.25, U1.19
/A7: J2.26, U1.22
/AREF: C3.1, J2.18, U1.20
/D0: J2.2, R2.2, U1.30
/D1: J2.1, R6.2, U1.31
/D2: J2.5, U1.32
/D3: J2.6, U1.1
/D4: J2.7, U1.2
/D5: J2.8, U1.9
/D6: J2.9, U1.10
/D7: J2.10, U1.11
/D8: J2.11, U1.12
/D9: J2.12, U1.13
/D10: J2.13, U1.14
/D11: J1.4, J2.14, U1.15
/D12: J1.3, J2.15, U1.16
/D13: J1.2, J2.16, R8.2, U1.17
/RESET: C2.2, J1.5, J2.3, J2.28, R1.2, SW1.2, U1.29
/RX: R2.1, R5.1, U2.1
/TX: Q1.1, R6.1
GND: C1.2, C3.2, C4.2, C5.2, C6.2, D1.2, D2.2, J1.6, J2.4, J2.29, L1.1, L2.1, Q1.2, SW1.1, U1.3, U1.5, U1.21, U1.33, U2.3, U2.4, U2.5, U3.1, X1.3
unnamed: C2.1, R4.1, U2.7
unnamed: D1.1, R5.2, U2.2
unnamed: D2.1, R4.2, U2.6
unnamed: L1.2, R7.1
unnamed: L2.2, R8.1
unnamed: L3.1, Q1.3
unnamed: L3.2, R3.1
unnamed: U1.7, X1.2
unnamed: U1.8, X1.1
VCC: J1.1, J2.30, U3.3

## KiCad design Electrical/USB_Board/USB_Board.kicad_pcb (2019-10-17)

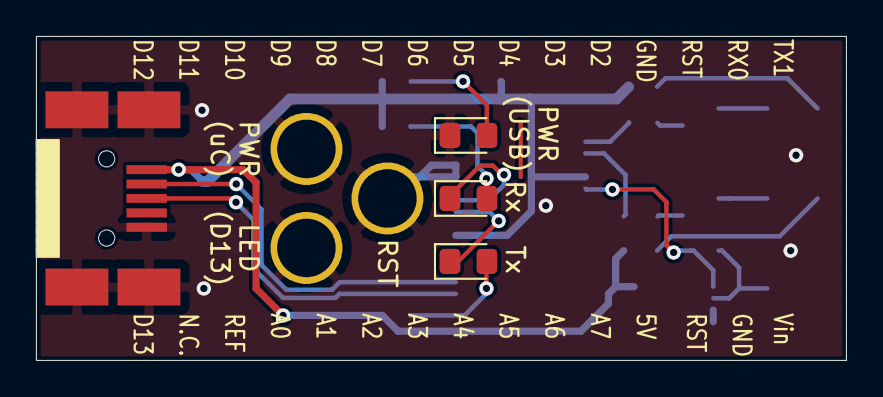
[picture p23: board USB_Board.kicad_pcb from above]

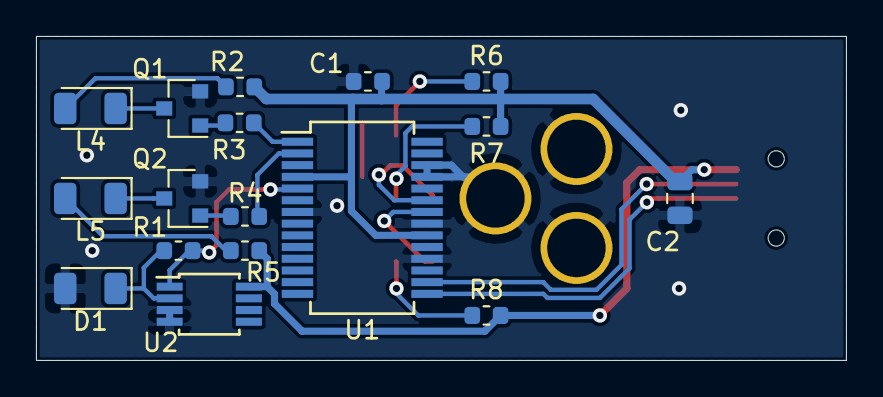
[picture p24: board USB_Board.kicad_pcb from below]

Board: 2 copper layers, 45.0 x 18.0 mm, 24 parts (17 on the bottom side), 19 nets.

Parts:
C1: 100 nF; C_0603_1608Metric
C2: 4.7uF; C_0805_2012Metric
D1: PD_RX; D_1206_3216Metric
H1, H2: light_pipe
H3: Switch; light_pipe
J1: USB_B_Mini; Molex_67503-1020
L1: blue; LED_0805_2012Metric_Pad1.15x1.40mm_HandSolder
L2: red; LED_0805_2012Metric_Pad1.15x1.40mm_HandSolder
L3: green; LED_0805_2012Metric_Pad1.15x1.40mm_HandSolder
L4: IR_TX; LED_1206_3216Metric
L5: IR_DTR; LED_1206_3216Metric
Q1, Q2: BC850; SOT-23
R1, R2, R5, R7, R8: R; R_0603_1608Metric
R3, R4: 4.7k; R_0603_1608Metric
R6: R_US; R_0603_1608Metric
U1: FT232RL; SSOP-28_5.3x10.2mm_P0.65mm
U2: OPA2381; MSOP-8_3x3mm_P0.65mm

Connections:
+5V: C1.1, C2.1, J1.1, R2.2, R5.2, R6.2, R7.2, R8.2, U1.4, U1.20, U2.8
/DTR: R4.1, U1.2
GND: C1.2, C2.2, D1.2, H1.1, H2.1, H3.1, J1.5, J1.6, L1.1, Q1.2, Q2.2, U1.7, U1.18, U1.21, U1.25, U1.26, U2.3, U2.4
unnamed: D1.1, R1.2, U2.2
unnamed: J1.2, U1.16
unnamed: J1.3, U1.15
unnamed: L1.2, R6.1
unnamed: L2.1, U1.23
unnamed: L2.2, R7.1
unnamed: L3.1, U1.22
unnamed: L3.2, R8.1
unnamed: L4.1, Q1.3
unnamed: L4.2, R2.1
unnamed: L5.1, Q2.3
unnamed: L5.2, R5.1
unnamed: Q1.1, R3.2
unnamed: Q2.1, R4.2
unnamed: R1.1, U1.5, U2.1
unnamed: R3.1, U1.1

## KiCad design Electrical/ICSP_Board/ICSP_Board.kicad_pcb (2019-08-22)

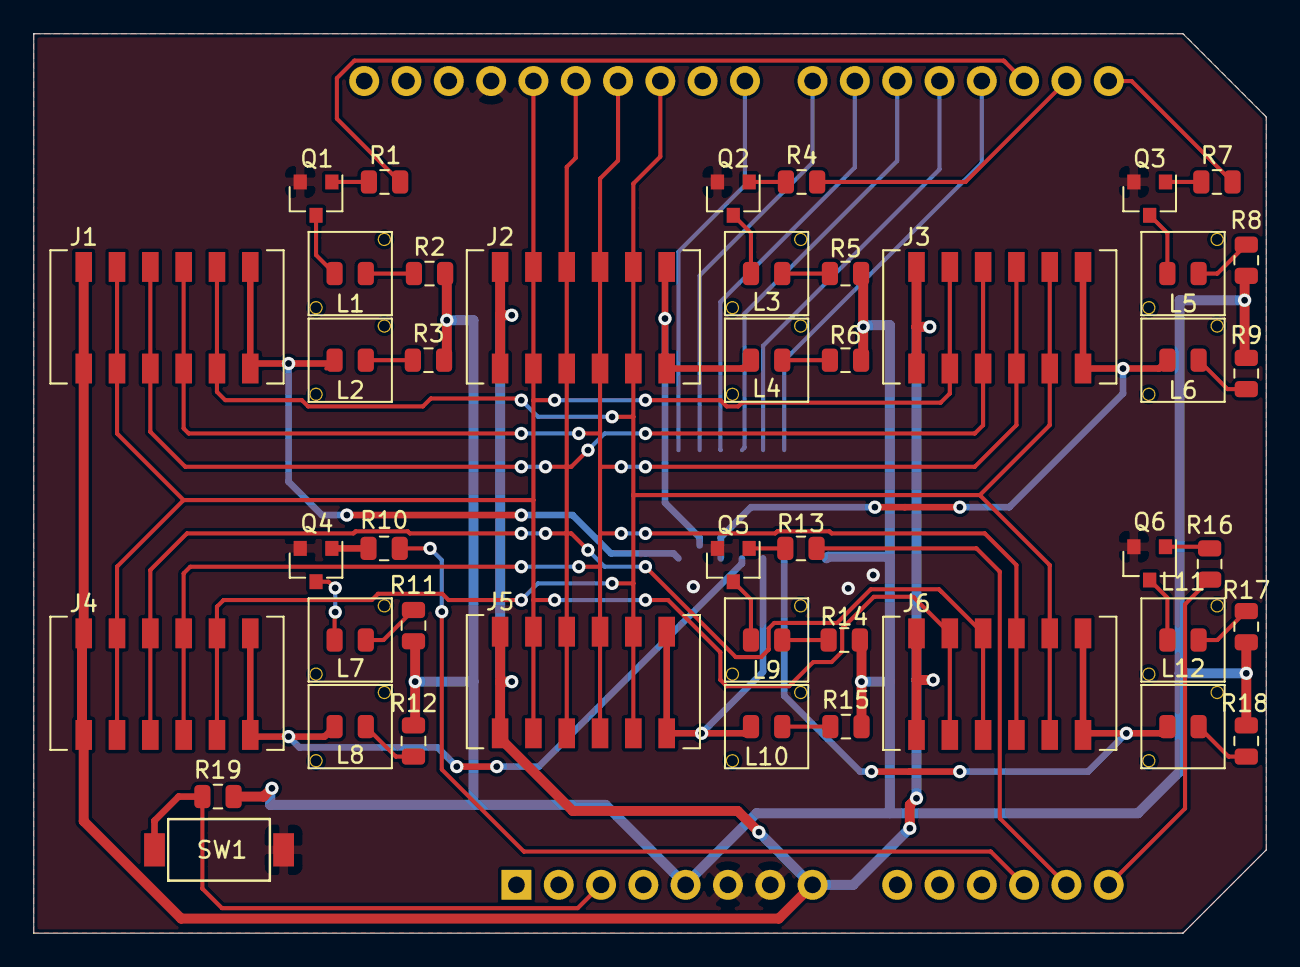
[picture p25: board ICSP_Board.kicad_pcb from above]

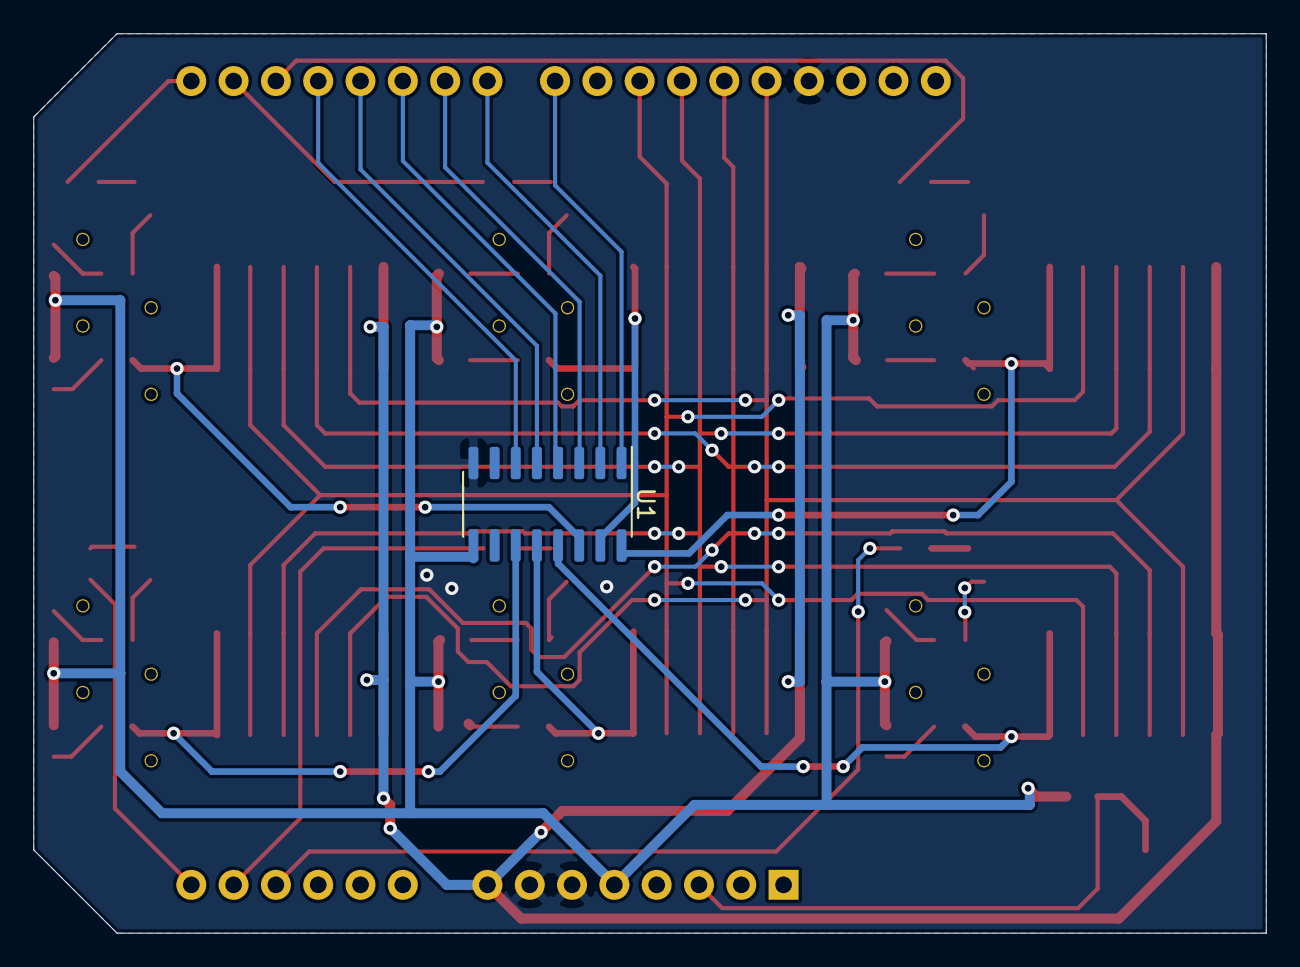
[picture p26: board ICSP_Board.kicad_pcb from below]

Board: 2 copper layers, 74.0 x 54.0 mm, 46 parts (2 on the bottom side), 50 nets.

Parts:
A1: Arduino_UNO_R3
J1, J2, J3, J4, J5, J6: AVX 009159006551906; card_edge_6p
L1, L3, L5, L7, L9, L11: gLED; LED_0805_LightPipe
L2, L4, L6, L8, L10, L12: rLED; LED_0805_LightPipe
Q1, Q2, Q3, Q4, Q5, Q6: BC850; SOT-23
R1, R2, R3, R4, R5, R6, R7, R8, R9, R10, R11, R12, R13, R14, R15, R16, R17, R18, R19: R_US; R_0805_2012Metric
SW1: SW_Push; PTS636-G-2.5-NoGND
U1: ULN2003A; SOIC-16_3.9x9.9mm_P1.27mm

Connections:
+5V: A1.5, R2.1, R3.1, R5.1, R6.1, R8.1, R9.1, R11.1, R12.1, R14.1, R15.1, R17.1, R18.1, R19.1, U1.9
/G1: L1.1, Q1.3
/G2: L3.1, Q2.3
/G3: L5.1, Q3.3
/G4: L7.1, Q4.3
/G5: L9.1, Q5.3
/G6: L11.1, Q6.3
/MISO: A1.27, J1.3, J2.3, J3.3, J4.3, J5.3, J6.3
/MOSI: A1.26, J1.4, J2.4, J3.4, J4.4, J5.4, J6.4
/RST: A1.25, J1.5, J2.5, J3.5, J4.5, J5.5, J6.5
/SCK: A1.28, J1.2, J2.2, J3.2, J4.2, J5.2, J6.2
/SW1: A1.3, R19.2, SW1.2
/ULN11: J6.6, L12.1, U1.11
/ULN12: J5.6, L10.1, U1.12
/ULN13: J4.6, L8.1, U1.13
/ULN14: J3.6, L6.1, U1.14
/ULN15: J2.6, L4.1, U1.15
/ULN16: J1.6, L2.1, U1.16
GND: A1.6, A1.7, A1.29, Q1.2, Q2.2, Q3.2, Q4.2, Q5.2, Q6.2, SW1.1, U1.8
unnamed: A1.12, R10.1
unnamed: A1.13, R13.1
unnamed: A1.14, R16.1
unnamed: A1.15, R7.1
unnamed: A1.16, R4.1
unnamed: A1.17, R1.1
unnamed: A1.18, U1.6
unnamed: A1.19, U1.5
unnamed: A1.20, U1.4
unnamed: A1.21, U1.3
unnamed: A1.22, U1.2
unnamed: A1.23, U1.1
unnamed: L1.2, R2.2
unnamed: L2.2, R3.2
unnamed: L3.2, R5.2
unnamed: L4.2, R6.2
unnamed: L5.2, R8.2
unnamed: L6.2, R9.2
unnamed: L7.2, R11.2
unnamed: L8.2, R12.2
unnamed: L9.2, R14.2
unnamed: L10.2, R15.2
unnamed: L11.2, R17.2
unnamed: L12.2, R18.2
unnamed: Q1.1, R1.2
unnamed: Q2.1, R4.2
unnamed: Q3.1, R7.2
unnamed: Q4.1, R10.2
unnamed: Q5.1, R13.2
unnamed: Q6.1, R16.2
VCC: A1.8, J1.1, J2.1, J3.1, J4.1, J5.1, J6.1

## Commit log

2019-08-10 Created libraries.
    [ICSP.kicad_pcb, ICSP.sch]
2019-08-10 added usb port, and ft232RL to PCB
    [USB_Board_1.kicad_pcb, USB_Board_1.sch]
2019-08-10 started board 2, made a few new parts
    [micro_board.kicad_pcb, micro_board.sch]
2019-08-10 Update USB_Board_1.sch
    made the sch cleaner
    [USB_Board_1.sch]
2019-08-10 added 3.3v regulator
    [micro_board.sch]
2019-08-10 Update USB_Board_1.sch
    added symbols for led and photodiodes: no footprints selected
    [USB_Board_1.sch]
2019-08-10 Added BOM for ICSP board.
    [BOM.csv]
2019-08-10 Update Bom.csv with FT232RL and MF-MSMF 050
    [BOM.csv]
2019-08-10 updated footprint for led
    [USB_Board_1.sch]
2019-08-10 assigned footprints and began creating footprint for oscillator
    [micro_board.sch]
2019-08-10 End of Saturday stream.
    [USB_Board_1.sch, micro_board.sch]
2019-08-11 Restructured repository.
    [BOM.csv, ICSP.kicad_pcb, ICSP.sch, USB_Board_1.kicad_pcb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]
2019-08-11 fixed symbol issue
    [USB_Board_1.sch]
2019-08-11 added reset leds, relabeled schmatic symbols for readablitiy.
    [USB_Board_1.sch]
2019-08-11 added ICSP, need to add LED and PD
    [micro_board.sch]
2019-08-11 added BOMs for uC and USB board
    [BOM_adi.csv, BOM_drfoland.csv, BOM_grace.csv]
2019-08-11 fixed transimpedence_photodiode connection on schematic
    [USB_Board_1.sch]
2019-08-11 added atmega footprint, started PCB
    [micro_board.kicad_pcb, micro_board.sch]
2019-08-11 assigned footprints to schematic
    [USB_Board_1.sch]
2019-08-11 Updated ICSP board.
    [ICSP.kicad_pcb, ICSP.sch]
2019-08-11 Finalized initial ICSP board layout.
    [ICSP.kicad_pcb, ICSP.sch]
2019-08-11 started pcb layout
    [micro_board.kicad_pcb, micro_board.sch]
2019-08-11 forgot to save before pushing
    [micro_board.kicad_pcb]
2019-08-12 Minor arduino nano footprint modifications.
    [micro_board.kicad_pcb]
2019-08-12 Updated schematic symbols.
    [USB_Board_1.sch]
2019-08-12 changed 3.3v regulator to 5v regulator, laid things out on pcb
    [micro_board.kicad_pcb, micro_board.sch]
2019-08-12 Completed r1 of USB Board.
    [USB_Board_1.sch]
2019-08-12 changed sizes of resistors and capacitors, trying to neatly lay things out on pcb
    [micro_board.kicad_pcb, micro_board.sch]
2019-08-12 Added light pipe package.
    [USB_Board_1.kicad_pcb, USB_Board_1.sch]
2019-08-12 trying to do stuff idk
    [micro_board.kicad_pcb]
2019-08-12 Updated LED locations on USB Board.
    [USB_Board_1.kicad_pcb, USB_Board_1.sch]
2019-08-12 locking in LED and PDs
    [micro_board.kicad_pcb, micro_board.sch]
2019-08-12 forgot to save earlier
    [micro_board.kicad_pcb]
2019-08-12 Updated uC board cuts and card edge contacts.
    [micro_board.kicad_pcb]
2019-08-13 updated BOM
    [BOM_grace.csv, micro_board.kicad_pcb]
2019-08-13 fixed tx connection to have transistor. gave myself a headache trying to figure out a good place to put the atmega
    [micro_board.kicad_pcb, micro_board.sch]
2019-08-15 Assisted with uC board component placement.
    [micro_board.kicad_pcb, micro_board.sch]
2019-08-15 Finished draft of USB board.
    [USB_Board_1.kicad_pcb, USB_Board_1.sch]
2019-08-15 adding traces, removed auto selector, changed diode footprints
    [micro_board.kicad_pcb]
2019-08-15 i have no idea where these last traces are supposed to go
    [micro_board.kicad_pcb, micro_board.sch]
2019-08-15 Fixed layout for USB board.
    [USB_Board_1.kicad_pcb, USB_Board_1.sch, USB_Board_1.step]
2019-08-15 forgot a file
    [micro_board.kicad_pcb]
2019-08-15 changed atmega, started re-laying traces
    [micro_board.kicad_pcb, micro_board.sch]
2019-08-17 finished first try of traces, problems with GND plane
    [micro_board.kicad_pcb, micro_board.sch]
2019-08-17 Finalized USB Board, inc. 3D models of light pipes.
    [MFFSMF050.stp, Molex67503-1020.stp, USB_Board_1.kicad_pcb, USB_Board_1.sch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]
2019-08-17 Deleted fuse from libraries because it is no longer in use.
    [MFFSMF050.stp]
2019-08-17 Finished draft of uC Board. Need to add 3D packages.
    [micro_board.kicad_pcb, micro_board.sch]
2019-08-19 Fixed part numbers on USB board.
    [USB_Board_1.kicad_pcb, USB_Board_1.sch]
2019-08-19 changed LED and PD footprints on USB boards
    [USB_Board_1.kicad_pcb, USB_Board_1.sch]
2019-08-19 Fixed footprints on uC board.
    [CSTNE16M0V530000R0--3DModel-STEP-56544.STEP, LM1117MP-3.3--3DModel-STEP-56544.STEP, PTS636SK25FSMTRLFS.stp, micro_board.kicad_pcb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]
2019-08-19 Fixed minor ground plane issues on uC Board.
    [micro_board.kicad_pcb, micro_board.sch]
2019-08-19 Added header pins to uC board 3D model.
    [Pin Header 1x15 TH Pitch 2.54mm.stp, micro_board.kicad_pcb]
2019-08-19 Cleaned up folders for USB and ICSP boards.
    [ICSP.kicad_pcb, ICSP_BOM.csv, USB_Board.kicad_pcb, USB_Board.sch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]
2019-08-21 Began exstablishing files for Mechanical design.
    [ICSP.kicad_pcb, ICSP.sch, USB_Board-B_SilkS.dxf, USB_Board-F_SilkS.dxf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]
2019-08-21 Prepared electrical models for mechanical assembly in FreeCAD.
    [AVX-00-9159-006-551-906.STEP, ICSP-B_SilkS.dxf, ICSP-F_SilkS.dxf, ICSP.kicad_pcb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]
2019-08-22 Fixed hole size on ICSP board.
    [ICSP_Board.kicad_pcb, USB_Board.FCStd, USB_Board.kicad_pcb, USB_Board.sch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]
2019-08-22 Initial ICSP housing rough cut.
    [ICSP_Board.kicad_pcb, ICSP_Board.sch, ICSP_Housing_top.stp]
2019-10-03 Created Housing Top for ICSP in FreeCAD (again).
    [ICSP_Housing_Top.FCStd, ICSP_Housing_top.stp]
2019-10-03 Completed upper-housing for ICSP.
    [ICSP_Housing_Top.FCStd, ICSP_Housing_Top.step]
2019-10-10 Began Hodgkin housing parts.
    [Hodgkin_Housing_Middle.FCStd, Hodgkin_Housing_Top.FCStd, Hodgkin_Housing_Top.step, Housing_Button.FCStd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]
2019-10-17 Updated BOMs.
    [Hodgkin_Housing_Middle.FCStd, ICSP_Housing_Top.FCStd, USB_Board_BOM.csv, uC_Board_BOM.csv]
2019-10-17 Updated transimpedance amp and rearranged USB board.
    [Hodgkin_Housing_Middle.FCStd, Hodgkin_Housing_Top.FCStd, Hodgkin_Housing_Top.step, Housing_Button.FCStd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]
2019-10-17 Remade the mechanical assemblies for the Hodgkin boards.
    [USB_Board.FCStd, uC_Board.FCStd, uC_Board_no_LightPipes.FCStd, uC_board-F_SilkS.dxf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]
2019-10-26 Finalized Housing.
    [Button.stl, Hodgkin_Housing_Middle.FCStd, Hodgkin_Housing_Top.FCStd, Hodgkin_Housing_Top.step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]
